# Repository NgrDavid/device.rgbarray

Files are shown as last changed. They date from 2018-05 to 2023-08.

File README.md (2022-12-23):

## Harp RGB Array

Controls 2 arrays of colored LEDs according to RGB scale (Up to 32 LED on each array). Each LED has an associated index.

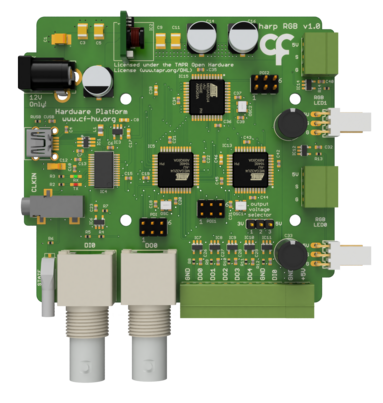
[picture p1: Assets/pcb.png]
harprgbarray


### Key Features ###

* Supports two LED array stripes
* Each stripe can have up to 32 LEDs
* Configurable color and intensity of each LED

### Connectivity ###

* 1x clock sync input (CLKIN) [stereo jack]
* 1x USB (for computer) [USB type C]
* 1x 12V supply [barrel connector jack]
* 1x I/O interface (5x general-purpose digital outputs DO0-DO4, 1x general purpose digital input DI0) [screw terminal]
* 1x digital output (DO0) [BNC]
* 1x digital input (DI0) [BNC]
* 1x Array 0 (G, S, 5V) [flick lock and screw terminal]
* 1x Array 1 (G, S, 5V) [flick lock and screw terminal]

## Interface ##

The interface with the Harp board can be done through [Bonsai](https://bonsai-rx.org/) or a dedicated GUI (Graphical User Interface).

In order to use this GUI, there are some software that needs to be installed:

1 - Install the [drivers](https://bitbucket.org/fchampalimaud/downloads/downloads/UsbDriver-2.12.26.zip).

2 - Install the [runtime](https://bitbucket.org/fchampalimaud/downloads/downloads/Runtime-1.0.zip).

3 - Reboot the computer.

4 - Install the [GUI](https://bitbucket.org/fchampalimaud/downloads/downloads/Harp%20RGB%20Array%20v1.0.0.zip).

## Licensing ##

Each subdirectory will contain a license or, possibly, a set of licenses if it involves both hardware and software.

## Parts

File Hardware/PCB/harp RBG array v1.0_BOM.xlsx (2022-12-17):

Part(s) | Quantity | Description | Distributor | Part. No.
IC1 | 1 | ESD Protection Low Cap | Mouser | 511-USBLC6-2SC6Y
IC2 | 1 | Conversores CC/CC sem isolação 6-A 4.5V-14V Input Non-Iso Adj Pwr Mod | Mouser | 595-PTR08060WVD
IC3 | 1 | LDO 250mA Ultra-Lo Noise LDO Reg | Mouser | 595-LP5907MFX-3.3NPB
IC4 | 1 | IC USB USB to Serial UART Enhanced IC SSOP-28 | Mouser | 895-FT232RL
IC5 | 1 | Microcontroladores de 8 bits - MCU 44TQFP, IND TEMP GREEN, 1.6-3.6V | Mouser | 556-ATXMEGA128A4U-AU
IC13, IC15 | 2 | Microcontroladores de 8 bits - MCU AVR8 32KB FLSH 4KB | Mouser | 556-ATXMEGA32A4U-AU
IC6, IC7, IC8, IC9, IC10, IC11, IC12, IC14 | 8 | Buffers e line drivers 1.65-5.5V Single Non-Inverting TTL | Mouser | 863-M74VHC1GT50DTT1G
C6, C7 | 2 | CAP CER 47pF 50V ±5% C0G 0402 | Mouser | 77-VJ0402A470JXACBC
CUSB | 1 | CAP CER 4.7nF 100V ±10% X7R 0402 | Mouser | 81-GRM155R72A472KA01
C4, C10, C13, C15, C18, C19, C21, C22, C23, C24, C26, C27, C28, C29, C30, C31, C32, C34, C35, C37, C39, C40, C42, C43, C45 | 25 | CAP CER 100nF 10V X5R 0402 | REEL | REEL
C20, C36, C44 | 3 | CAP CER 0.33uF 10V ±10% X5R 0402 | Mouser | GRM155R61A334KE15D
C12 | 1 | CAP TAN 4.7uF 6.3V ±10% 1206 | Mouser | 80-T491A475K006
C8, C17, C25, C38, C46 | 5 | CAP CER 10uF 10V ±10% X5R 0603 | Mouser | 81-GRM188R61A106KE9D
C1 | 1 | CAP TAN 22uF 20V ±10% 1210 | Mouser | 667-20TQC22MYFB
C9 | 1 | CAP CER 22uF 16V ±10% X5R 1210 | Mouser | 81-GRM32ER61C226KE20
C3, C5 | 2 | CAP CER 22uF 25V ±10% X5R 1210 | Mouser | 81-GRM32ER61E226KE15
C2 | 1 | CAP ELE 100uF 25V ±20% | Mouser | 667-25SVF100M
C14, C16 | 2 | CAP ELE 270uF 16V ±20% | Mouser | 667-16SVF270M
C33, C41 | 2 | CAP ELE TH 470uF 16V 20% | Mouser | 667-EEU-FM1C471
R7, R8, R9, R10, R11, R12 | 6 | RES SMD 33Ω 5% 0402 | Mouser | 667-ERJ-2GEJ330X
R6 | 1 | RES SMD 68Ω 5% 0402 | Mouser | 71-CRCW0402-68-E3
R13, R14 | 2 | RES SMD 100Ω 1% 0402 | Mouser | 667-ERJ-2RKF1000X
RTRIM | 1 | RES SMD 267Ω 1% 0402 | Mouser | 667-ERJ-2RKF2670X
R4 | 1 | RES SMD 330Ω 1% 0402 | Mouser | 667-ERJ-PA2F3300X
R5 | 1 | RES SMD 100kΩ 1% 0402 | REEL | REEL
RUSB | 1 | RES SMD 1MΩ 1% 0402 | Mouser | 652-CR0402FX-1004GLF
STATE | 1 | LED, Green, 1.6mm x 0.8mm, 566 nm, 2.1 V, 20 mA, 15 mcd | Mouser | 78-TLMP1100-GS08
OSC, OSC1, OSC2 | 3 | 32MHz 10ppm | Mouser | 998-1001CI5032.0000T
CLKIN | 1 | SMT 3.5 STEREO REEL | Mouser | 502-35RASMT2BHNTRX
L1 | 1 | 40ohms 100MHz 1.5A Monolithic 0805 SMD | Mouser | 875-MI0805K400R-10
L2 | 1 | FERRITE BEAD 600Ω 500mA 300mΩ 0805 | Mouser | 875-HZ0805E601R-10
PDI, PDI1, PDI2 | 3 | 6P DR UNSHRD HRD | Mouser | 649-67996-206HLF
USB | 1 | UX60-MB-5S8 | Mouser | 798-UX60-MB-5S8
USB Cable | 1 | USB A - MINI-B 1M BLACK | Mouser | 538-88732-8602
 | 1 | Tubos de Luz LED CML LIGHTPIPE | Mouser | 606-7513D2-L
JACK | 1 | CC PCB 2.1MM | Mouser | 163-179PH-EX
IN1, OUT1 | 2 | Connectores RF / Connectores Coaxiais R.A. JACK 50 OHM | Mouser | 571-5227161-1
JP1 | 1 | 3POS Gold Male | Mouser | 649-68001-203HLF
 | 1 | SHUNT JUMPER, 2POS | Farnell | 2396301
WALL ADAPTER | 1 | AC/DC Power Supply, Level VI, Wall Mount, 1 Output, 24 W, 12 V, 2 A | Farnell | 2643258
J1, J2 | 2 | Right Angle, 2.54 mm, 3 Contacts, Header, KK 7395 Series, Through Hole | Farnell | 1360143
X2 | 1 | 20.1550M/2-E - Pluggable Terminal Block, 3.5 mm, 2 Ways, 28 AWG, 16 AWG, 1.5 mm², Screw | Farnell | 2575215
X3, X4 | 2 | 20.1550M/3-E - Pluggable Terminal Block, 3.5 mm, 3 Ways, 28 AWG, 16 AWG, 1.5 mm², Screw | Farnell | 2575216
X1 | 1 | 20.1550M/8-E - Pluggable Terminal Block, 3.5 mm, 8 Ways, 28 AWG, 16 AWG, 1.5 mm², Screw | Farnell | 2575220
 | 1 | 20.155MH/3-E - Terminal Block, Horizontal, Header, 3.5 mm, 3 Ways, 10 A | Farnell | 2517859
 | 2 | 20.155MH/2-E - Terminal Block, Horizontal, Header, 3.5 mm, 2 Ways, 10 A | Farnell | 2517858
 | 1 | 20.155MH/8-E - Terminal Block, Horizontal, Header, 3.5 mm, 8 Ways, 10 A | Farnell | 2517863
 | 8 | 1110030 - Nut, Hex, M3, Nylon 6.6, Pack of 50 | Farnell | 1110030
 | 4 | Machine Screw, M3, 10 mm, Nylon (Polyamide), Pan Head Slotted, PK25 | Farnell | 1514410
Components | 115
Licensed under the TAPR Open Hardware License (www.tapr.org/OHL)
Copyright 2017 Artur Silva and Filipe Carvalho

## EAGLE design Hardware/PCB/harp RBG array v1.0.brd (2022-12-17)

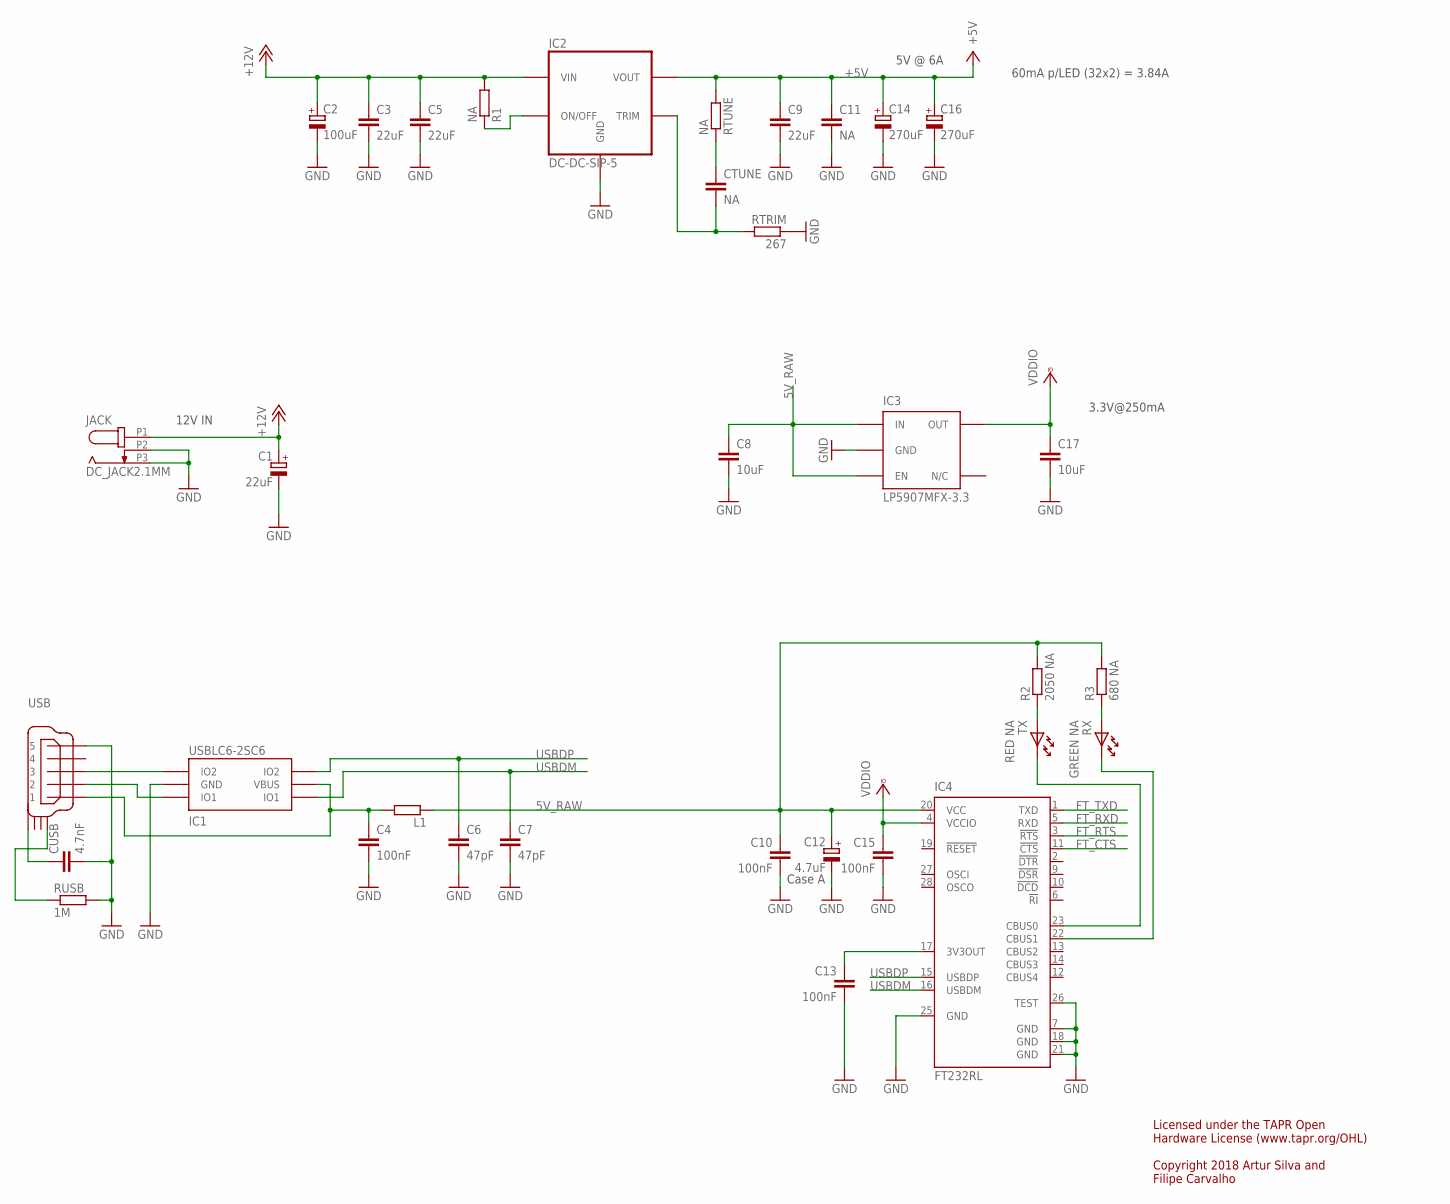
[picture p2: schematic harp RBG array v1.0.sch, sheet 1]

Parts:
C1: 22uF; CAP_100UF_HAND
C2: 100uF; PANASONIC_E
C3, C5, C9: 22uF; C1210
C4, C10, C13, C15: 100nF; C0402
C6, C7: 47pF; C0402
C8, C17: 10uF; C0603
C11: NA; C1210
C12: 4.7uF; A/3216-18W
C14, C16: 270uF; PANASONIC_E
CTUNE: NA; C0402
CUSB: 4.7nF; C0402
IC1: USBLC6-2SC6; SOT23-6L
IC2: DC-DC-SIP-5; SIP-5
IC3: LP5907MFX-3.3; TSOT23-5
IC4: FT232RL; SSOP28
JACK: DC_JACK2.1MM; DC_POWER_INPUT_2.1MM
L1: ???; R0805
R1: NA; R0402
R2: 2050 NA; R0402
R3: 680 NA; R0402
RTRIM: 267; R0402
RTUNE: NA; R0402
RUSB: 1M; R0402
RX: GREEN NA; LED_HAND
TX: RED NA; LED_HAND
USB: USB_MINI_B; 240-0002-1

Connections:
5V_RAW: C8.1, C10.1, C12.+, IC3.1 (IN), IC3.3 (EN), IC4.20 (VCC), L1.1, R2.2, R3.2
+5V: C9.1, C11.1, C14.+, C16.+, IC2.P4 (VOUT), RTUNE.2; also elsewhere on the board
+12V: C1.+, C2.+, C3.1, C5.1, IC2.P2 (VIN), JACK.P1 (1), R1.2
FT_CTS: IC4.11 (!CTS); also elsewhere on the board
FT_RTS: IC4.3 (!RTS); also elsewhere on the board
FT_RXD: IC4.5 (RXD); also elsewhere on the board
FT_TXD: IC4.1 (TXD); also elsewhere on the board
GND: C1.-, C2.-, C3.2, C4.2, C5.2, C6.2, C7.2, C8.2, C9.2, C10.2, C11.2, C12.-, C13.2, C14.-, C15.2, C16.-, C17.2, CUSB.2, IC1.P$2 (GND), IC2.P3 (GND), IC3.2 (GND), IC4.7 (GND), IC4.18 (GND), IC4.21 (GND), IC4.25 (GND), IC4.26 (TEST), JACK.P2 (2), JACK.P3 (3), RTRIM.1, RUSB.2, USB.P$5 (5); also elsewhere on the board
unnamed: CTUNE.2, IC2.P5 (TRIM), RTRIM.2
unnamed: CTUNE.1, RTUNE.1
unnamed: IC2.P1 (ON/OFF), R1.1
unnamed: C13.1, IC4.17 (3V3OUT)
unnamed: C4.1, IC1.P$5 (VBUS), L1.2, USB.P$1 (1)
unnamed: IC1.P$1 (IO1), USB.P$2 (2)
unnamed: R3.1, RX.A
unnamed: IC4.23 (CBUS0), TX.K
unnamed: IC4.22 (CBUS1), RX.K
unnamed: IC1.P$3 (IO2), USB.P$3 (3)
unnamed: CUSB.1, USB.SHIELD_4
unnamed: RUSB.1, USB.SHIELD_1
unnamed: R2.1, TX.A
USBDM: C7.1, IC1.P$6 (IO1), IC4.16 (USBDM)
USBDP: C6.1, IC1.P$4 (IO2), IC4.15 (USBDP)
VCCIO: C15.1, C17.1, IC3.5 (OUT), IC4.4 (VCCIO); also elsewhere on the board

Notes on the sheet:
Case A
3.3V@250mA
Licensed under the TAPR Open Hardware License (www.tapr.org/OHL) Copyright 2018 Artur Silva and Filipe Carvalho
12V IN
5V @ 6A
60mA p/LED (32x2) = 3.84A

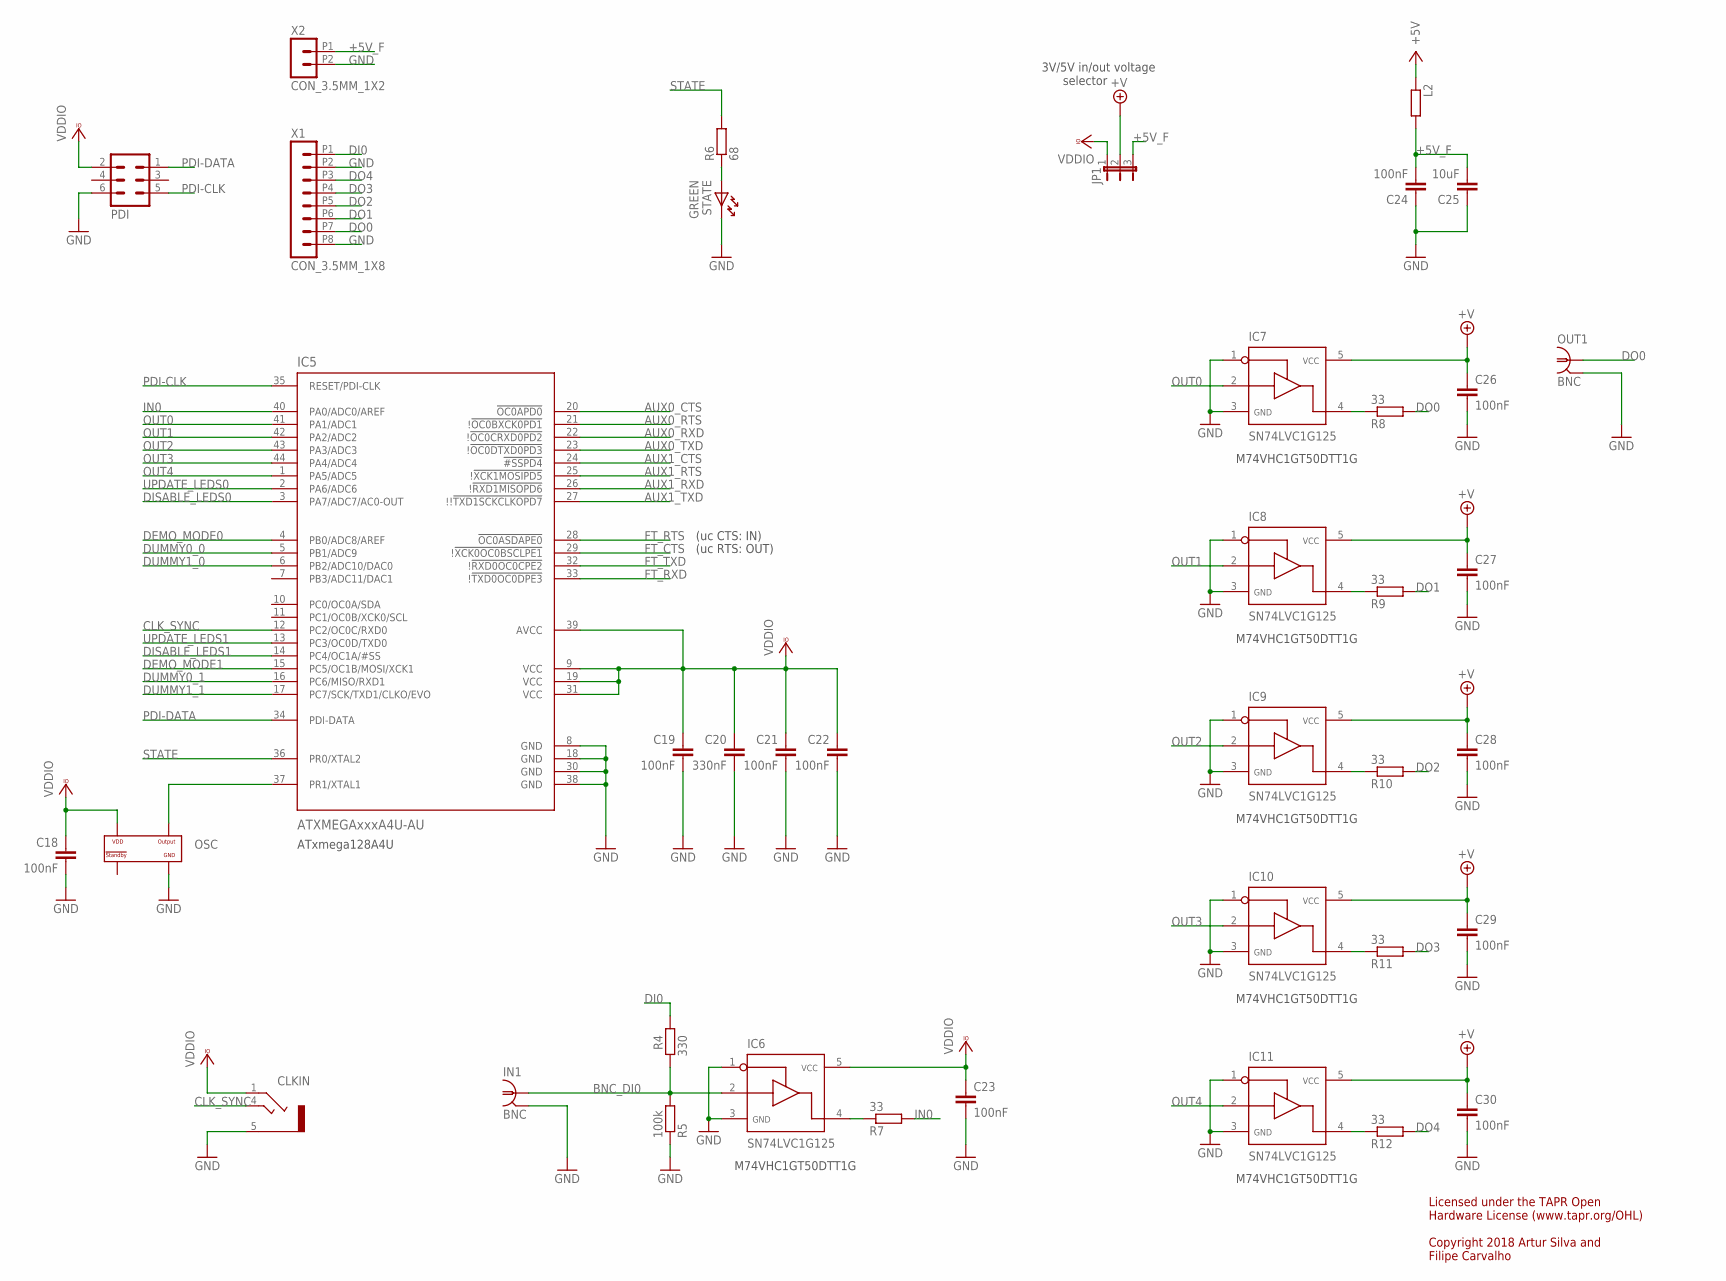
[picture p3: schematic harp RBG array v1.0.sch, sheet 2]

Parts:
C18, C19, C21, C22, C23, C24, C26, C27, C28, C29, C30: 100nF; C0402
C20: 330nF; C0402
C25: 10uF; C0603
CLKIN: STEREO_JACK; 35RASMT2BHNTRX
IC5: ATXMEGAxxxA4U-AU; QFP80P1200X1200X120-44N
IC6, IC7, IC8, IC9, IC10, IC11: SN74LVC1G125; SOT23-5
IN1: BNC; BNC_RA
JP1: JP2E; JP2
L2: 600@100M; R0805
OSC: OSCILLATOR; OSCILLATOR_3.2X2.5
OUT1: BNC; BNC_RA
PDI: MA03-2
R4: 330; R0402
R5: 100k; R0402
R6: 68; R0402
R7, R8, R9, R10, R11, R12: 33; R0402
STATE: GREEN; LED_HAND
X1: CON_3.5MM_1X8
X2: CON_3.5MM_1X2

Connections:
+5V: L2.1; also elsewhere on the board
+5V_F: C24.2, C25.2, JP1.3, L2.2, X2.P1 (1)
+V: C26.1, C27.1, C28.1, C29.1, C30.1, IC7.5, IC8.5, IC9.5, IC10.5, IC11.5, JP1.2
AUX0_CTS: IC5.20 (!OC0APD0); also elsewhere on the board
AUX0_RTS: IC5.21 (!!OC0BXCK0PD1); also elsewhere on the board
AUX0_RXD: IC5.22 (!!OC0CRXD0PD2); also elsewhere on the board
AUX0_TXD: IC5.23 (!!OC0DTXD0PD3); also elsewhere on the board
AUX1_CTS: IC5.24 (!#SSPD4); also elsewhere on the board
AUX1_RTS: IC5.25 (!!XCK1MOSIPD5); also elsewhere on the board
AUX1_RXD: IC5.26 (!!RXD1MISOPD6); also elsewhere on the board
AUX1_TXD: IC5.27 (!!!TXD1SCKCLKOPD7); also elsewhere on the board
BNC_DI0: IC6.2, IN1.1, R4.2, R5.2
CLK_SYNC: CLKIN.4, IC5.12 (PC2/OC0C/RXD0)
DEMO_MODE0: IC5.4 (PB0/ADC8/AREF); also elsewhere on the board
DEMO_MODE1: IC5.15 (PC5/OC1B/MOSI/XCK1); also elsewhere on the board
DI0: R4.1, X1.P1 (1)
DISABLE_LEDS0: IC5.3 (PA7/ADC7/AC0-OUT); also elsewhere on the board
DISABLE_LEDS1: IC5.14 (PC4/OC1A/#SS); also elsewhere on the board
DO0: OUT1.1, R8.2, X1.P7 (7)
DO1: R9.2, X1.P6 (6)
DO2: R10.2, X1.P5 (5)
DO3: R11.2, X1.P4 (4)
DO4: R12.2, X1.P3 (3)
DUMMY0_0: IC5.5 (PB1/ADC9); also elsewhere on the board
DUMMY0_1: IC5.16 (PC6/MISO/RXD1); also elsewhere on the board
DUMMY1_0: IC5.6 (PB2/ADC10/DAC0); also elsewhere on the board
DUMMY1_1: IC5.17 (PC7/SCK/TXD1/CLKO/EVO); also elsewhere on the board
FT_CTS: IC5.29 (!!XCK0OC0BSCLPE1); also elsewhere on the board
FT_RTS: IC5.28 (!OC0ASDAPE0); also elsewhere on the board
FT_RXD: IC5.33 (!!TXD0OC0DPE3); also elsewhere on the board
FT_TXD: IC5.32 (!!RXD0OC0CPE2); also elsewhere on the board
GND: C18.2, C19.2, C20.2, C21.2, C22.2, C23.2, C24.1, C25.1, C26.2, C27.2, C28.2, C29.2, C30.2, CLKIN.5, IC5.8 (GND), IC5.18 (GND), IC5.30 (GND), IC5.38 (GND), IC6.1, IC6.3, IC7.1, IC7.3, IC8.1, IC8.3, IC9.1, IC9.3, IC10.1, IC10.3, IC11.1, IC11.3, IN1.2, OSC.P$2 (GND), OUT1.2, PDI.6, R5.1, STATE.K, X1.P2 (2), X1.P8 (8), X2.P2 (2); also elsewhere on the board
IN0: IC5.40 (PA0/ADC0/AREF), R7.2
unnamed: IC6.4, R7.1
unnamed: IC8.4, R9.1
unnamed: IC7.4, R8.1
unnamed: IC9.4, R10.1
unnamed: IC10.4, R11.1
unnamed: IC11.4, R12.1
unnamed: R6.1, STATE.A
OSC2: IC5.37 (PR1/XTAL1), OSC.P$3 (OUTPUT)
OUT0: IC5.41 (PA1/ADC1), IC7.2
OUT1: IC5.42 (PA2/ADC2), IC8.2
OUT2: IC5.43 (PA3/ADC3), IC9.2
OUT3: IC5.44 (PA4/ADC4), IC10.2
OUT4: IC5.1 (PA5/ADC5), IC11.2
PDI-CLK: IC5.35 (RESET/PDI-CLK), PDI.5
PDI-DATA: IC5.34 (PDI-DATA), PDI.1
STATE: IC5.36 (PR0/XTAL2), R6.2
UPDATE_LEDS0: IC5.2 (PA6/ADC6); also elsewhere on the board
UPDATE_LEDS1: IC5.13 (PC3/OC0D/TXD0); also elsewhere on the board
VCCIO: C18.1, C19.1, C20.1, C21.1, C22.1, C23.1, CLKIN.1, IC5.9 (VCC), IC5.19 (VCC), IC5.31 (VCC), IC5.39 (AVCC), IC6.5, JP1.1, OSC.P$4 (VDD), PDI.2; also elsewhere on the board

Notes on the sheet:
Licensed under the TAPR Open Hardware License (www.tapr.org/OHL) Copyright 2018 Artur Silva and Filipe Carvalho
(uc CTS: IN)
(uc RTS: OUT)
M74VHC1GT50DTT1G
3V/5V in/out voltage selector
ATxmega128A4U

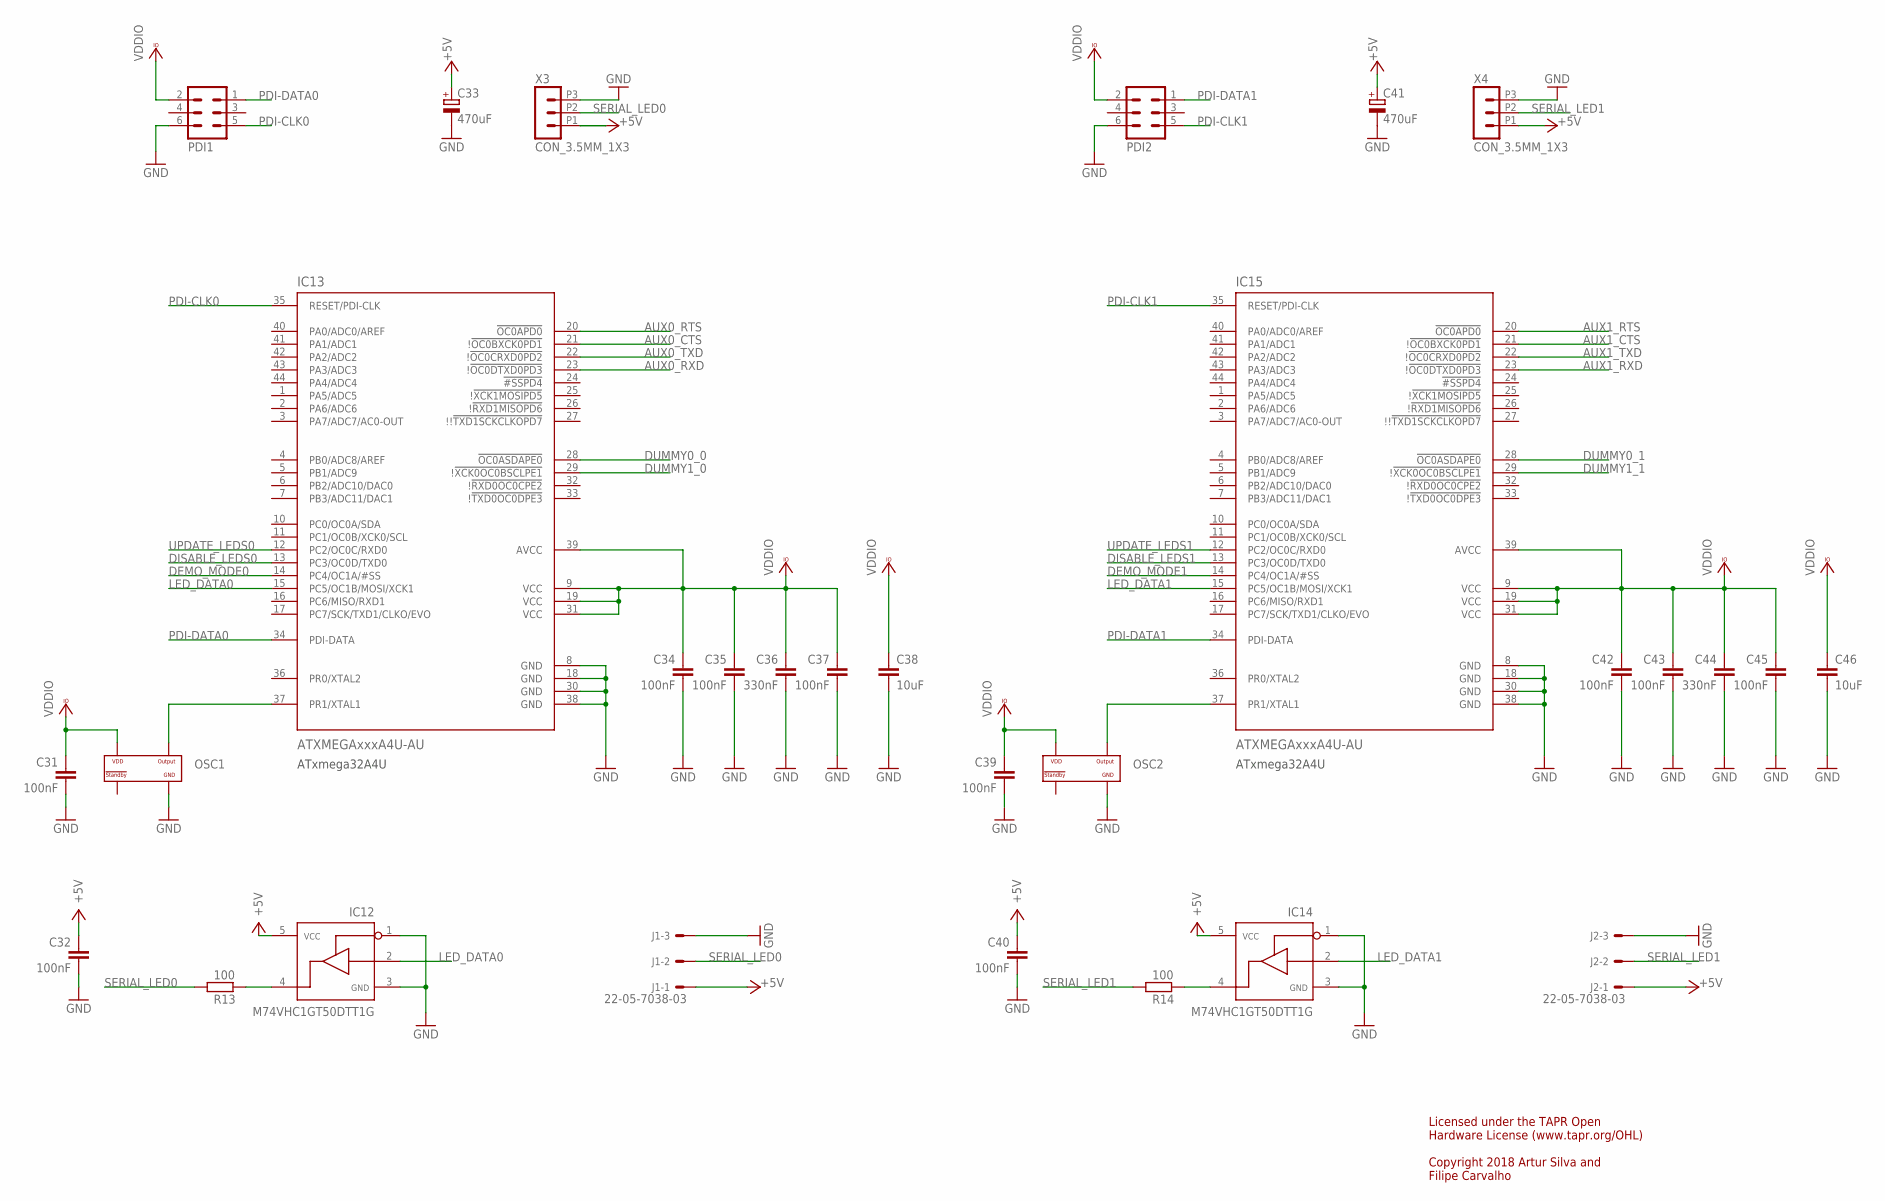
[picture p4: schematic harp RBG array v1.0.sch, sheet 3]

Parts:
C31, C32, C34, C35, C37, C39, C40, C42, C43, C45: 100nF; C0402
C33, C41: 470uF; E3,5-8
C36, C44: 330nF; C0402
C38, C46: 10uF; C0603
IC12, IC14: M74VHC1GT50DTT1G; SOT23-5
IC13, IC15: ATXMEGAxxxA4U-AU; QFP80P1200X1200X120-44N
J1, J2: 22-05-7038-03; 7395-03
OSC1, OSC2: OSCILLATOR; OSCILLATOR_3.2X2.5
PDI1, PDI2: MA03-2
R13, R14: 100; R0402
X3, X4: CON_3.5MM_1X3

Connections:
+5V: C32.1, C33.+, C40.1, C41.+, IC12.5, IC14.5, J1.1, J2.1, X3.P1 (1), X4.P1 (1); also elsewhere on the board
AUX0_CTS: IC13.21 (!!OC0BXCK0PD1); also elsewhere on the board
AUX0_RTS: IC13.20 (!OC0APD0); also elsewhere on the board
AUX0_RXD: IC13.23 (!!OC0DTXD0PD3); also elsewhere on the board
AUX0_TXD: IC13.22 (!!OC0CRXD0PD2); also elsewhere on the board
AUX1_CTS: IC15.21 (!!OC0BXCK0PD1); also elsewhere on the board
AUX1_RTS: IC15.20 (!OC0APD0); also elsewhere on the board
AUX1_RXD: IC15.23 (!!OC0DTXD0PD3); also elsewhere on the board
AUX1_TXD: IC15.22 (!!OC0CRXD0PD2); also elsewhere on the board
DEMO_MODE0: IC13.14 (PC4/OC1A/#SS); also elsewhere on the board
DEMO_MODE1: IC15.14 (PC4/OC1A/#SS); also elsewhere on the board
DISABLE_LEDS0: IC13.13 (PC3/OC0D/TXD0); also elsewhere on the board
DISABLE_LEDS1: IC15.13 (PC3/OC0D/TXD0); also elsewhere on the board
DUMMY0_0: IC13.28 (!OC0ASDAPE0); also elsewhere on the board
DUMMY0_1: IC15.28 (!OC0ASDAPE0); also elsewhere on the board
DUMMY1_0: IC13.29 (!!XCK0OC0BSCLPE1); also elsewhere on the board
DUMMY1_1: IC15.29 (!!XCK0OC0BSCLPE1); also elsewhere on the board
GND: C31.2, C32.2, C33.-, C34.2, C35.2, C36.2, C37.2, C38.2, C39.2, C40.2, C41.-, C42.2, C43.2, C44.2, C45.2, C46.2, IC12.1, IC12.3, IC13.8 (GND), IC13.18 (GND), IC13.30 (GND), IC13.38 (GND), IC14.1, IC14.3, IC15.8 (GND), IC15.18 (GND), IC15.30 (GND), IC15.38 (GND), J1.3, J2.3, OSC1.P$2 (GND), OSC2.P$2 (GND), PDI1.6, PDI2.6, X3.P3 (3), X4.P3 (3); also elsewhere on the board
LED_DATA0: IC12.2, IC13.15 (PC5/OC1B/MOSI/XCK1)
LED_DATA1: IC14.2, IC15.15 (PC5/OC1B/MOSI/XCK1)
unnamed: IC14.4, R14.2
unnamed: IC12.4, R13.2
OSC1: IC13.37 (PR1/XTAL1), OSC1.P$3 (OUTPUT)
OSC3: IC15.37 (PR1/XTAL1), OSC2.P$3 (OUTPUT)
PDI-CLK0: IC13.35 (RESET/PDI-CLK), PDI1.5
PDI-CLK1: IC15.35 (RESET/PDI-CLK), PDI2.5
PDI-DATA0: IC13.34 (PDI-DATA), PDI1.1
PDI-DATA1: IC15.34 (PDI-DATA), PDI2.1
SERIAL_LED0: J1.2, R13.1, X3.P2 (2)
SERIAL_LED1: J2.2, R14.1, X4.P2 (2)
UPDATE_LEDS0: IC13.12 (PC2/OC0C/RXD0); also elsewhere on the board
UPDATE_LEDS1: IC15.12 (PC2/OC0C/RXD0); also elsewhere on the board
VCCIO: C31.1, C34.1, C35.1, C36.1, C37.1, C38.1, C39.1, C42.1, C43.1, C44.1, C45.1, C46.1, IC13.9 (VCC), IC13.19 (VCC), IC13.31 (VCC), IC13.39 (AVCC), IC15.9 (VCC), IC15.19 (VCC), IC15.31 (VCC), IC15.39 (AVCC), OSC1.P$4 (VDD), OSC2.P$4 (VDD), PDI1.2, PDI2.2; also elsewhere on the board

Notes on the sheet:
ATxmega32A4U
Licensed under the TAPR Open Hardware License (www.tapr.org/OHL) Copyright 2018 Artur Silva and Filipe Carvalho

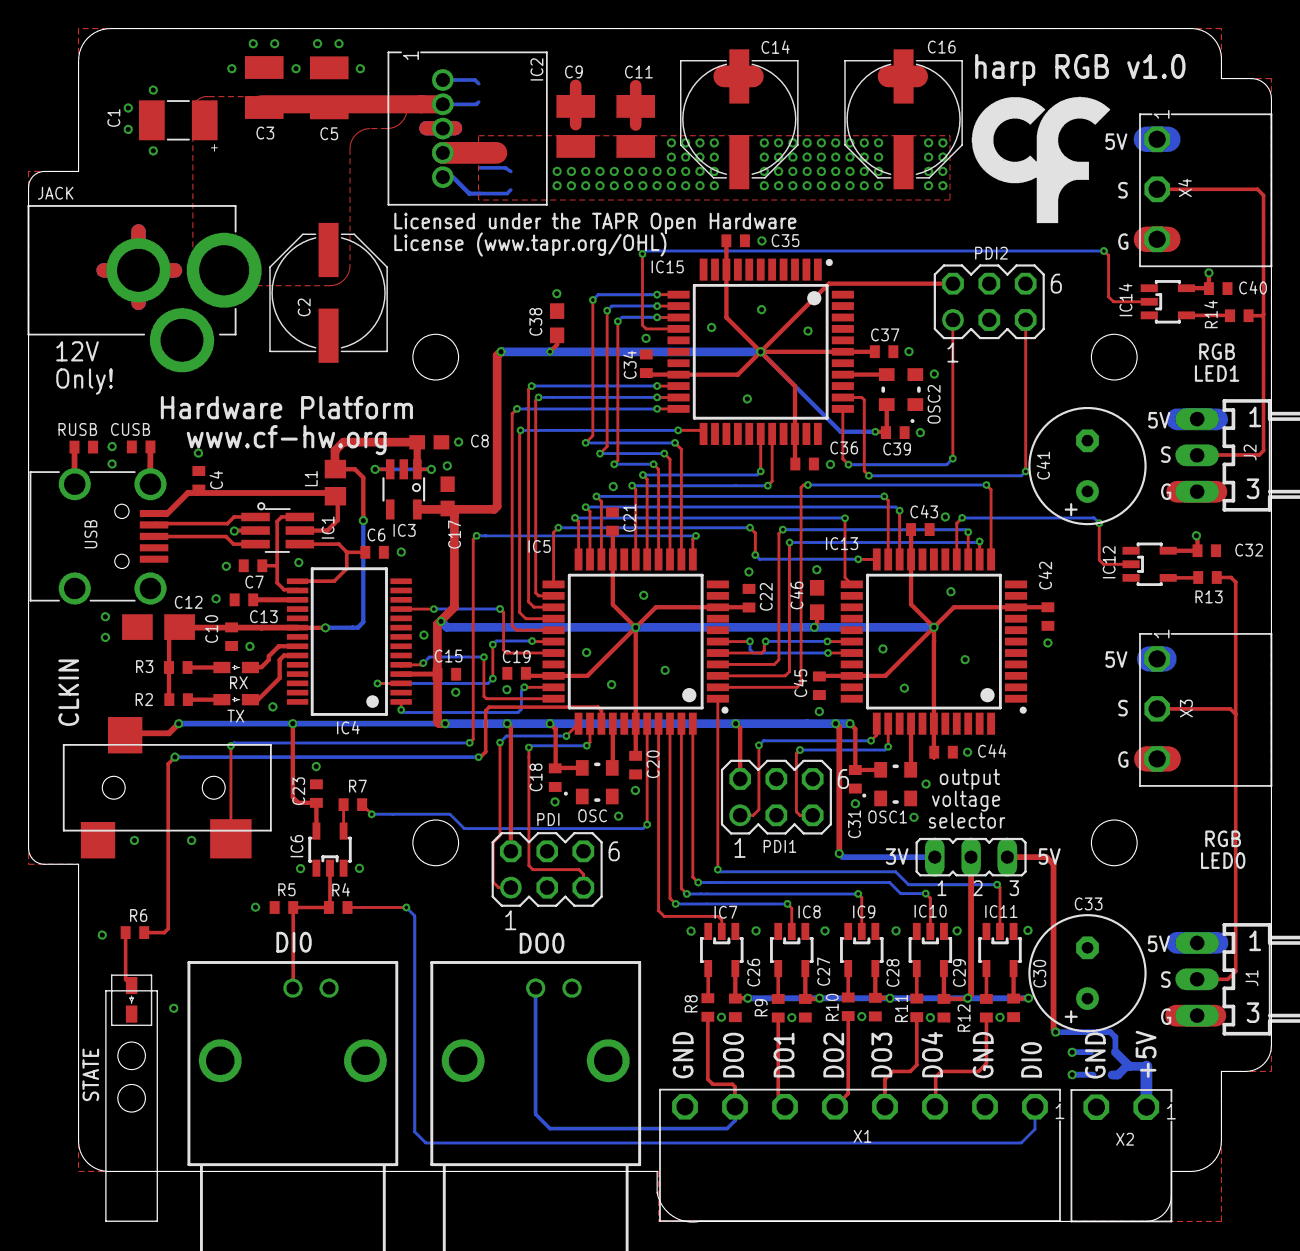
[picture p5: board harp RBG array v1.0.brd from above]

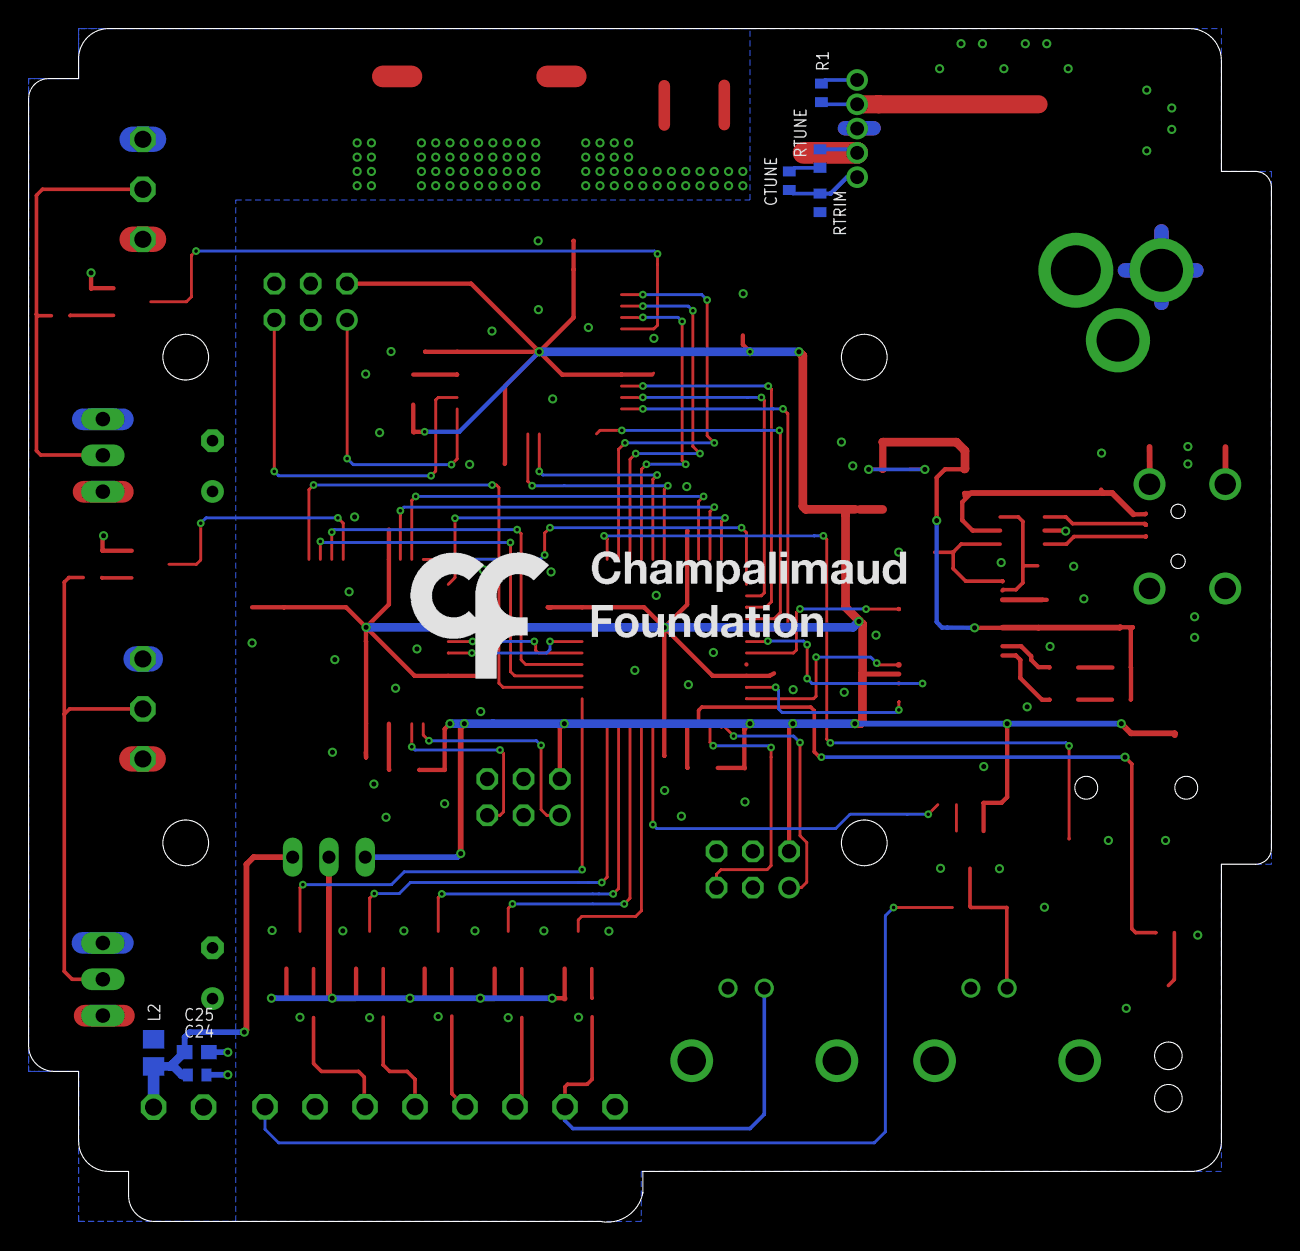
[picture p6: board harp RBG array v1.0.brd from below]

Board: 2 copper layers, 87.0 x 83.5 mm, 106 parts (8 on the bottom side), 81 nets.

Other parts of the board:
U$1: LED_PIPE_7513D2-L
U$3: LOGO_5
U$9: LOGO_6

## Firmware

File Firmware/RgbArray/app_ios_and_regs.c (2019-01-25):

#include <avr/io.h>
#include "hwbp_core_types.h"
#include "app_ios_and_regs.h"

/************************************************************************/
/* Configure and initialize IOs                                         */
/************************************************************************/
void init_ios(void)
{	/* Configure input pins */
	io_pin2in(&PORTA, 0, PULL_IO_UP, SENSE_IO_EDGES_BOTH);               // DI0
	io_pin2in(&PORTB, 1, PULL_IO_DOWN, SENSE_IO_EDGES_BOTH);             // DUMMY0_0
	io_pin2in(&PORTB, 2, PULL_IO_DOWN, SENSE_IO_EDGES_BOTH);             // DUMMY1_0
	io_pin2in(&PORTC, 6, PULL_IO_DOWN, SENSE_IO_EDGES_BOTH);             // DUMMY0_1
	io_pin2in(&PORTC, 7, PULL_IO_DOWN, SENSE_IO_EDGES_BOTH);             // DUMMY1_1

	/* Configure input interrupts */
	io_set_int(&PORTA, INT_LEVEL_LOW, 0, (1<<0), false);                 // DI0

	/* Configure output pins */
	io_pin2out(&PORTA, 1, OUT_IO_DIGITAL, IN_EN_IO_EN);                  // DO0
	io_pin2out(&PORTA, 2, OUT_IO_DIGITAL, IN_EN_IO_EN);                  // DO1
	io_pin2out(&PORTA, 3, OUT_IO_DIGITAL, IN_EN_IO_EN);                  // DO2
	io_pin2out(&PORTA, 4, OUT_IO_DIGITAL, IN_EN_IO_EN);                  // DO3
	io_pin2out(&PORTA, 5, OUT_IO_DIGITAL, IN_EN_IO_EN);                  // DO4
	io_pin2out(&PORTA, 6, OUT_IO_DIGITAL, IN_EN_IO_EN);                  // UPDATE_LEDS0
	io_pin2out(&PORTA, 7, OUT_IO_DIGITAL, IN_EN_IO_EN);                  // DISABLE_LEDS0
	io_pin2out(&PORTC, 3, OUT_IO_DIGITAL, IN_EN_IO_EN);                  // UPDATE_LEDS1
	io_pin2out(&PORTC, 4, OUT_IO_DIGITAL, IN_EN_IO_EN);                  // DISABLE_LEDS1
	io_pin2out(&PORTB, 0, OUT_IO_DIGITAL, IN_EN_IO_EN);                  // DEMO_MODE0
	io_pin2out(&PORTC, 5, OUT_IO_DIGITAL, IN_EN_IO_EN);                  // DEMO_MODE1
	io_pin2out(&PORTB, 0, OUT_IO_DIGITAL, IN_EN_IO_EN);                  // DEMO_MODE0
	io_pin2out(&PORTC, 5, OUT_IO_DIGITAL, IN_EN_IO_EN);                  // DEMO_MODE1

	/* Initialize output pins */
	clr_DO0;
	clr_DO1;
	clr_DO2;
	clr_DO3;
	clr_DO4;
	clr_UPDATE_LEDS0;
	clr_DISABLE_LEDS0;
	clr_UPDATE_LEDS1;
	clr_DISABLE_LEDS1;
	clr_DEMO_MODE0;
	clr_DEMO_MODE1;
	clr_DEMO_MODE0;
	clr_DEMO_MODE1;
}

/************************************************************************/
/* Registers' stuff                                                     */
/************************************************************************/
AppRegs app_regs;

uint8_t app_regs_type[] = {
	TYPE_U8,
	TYPE_U8,
	TYPE_U8,
	TYPE_U8,
	TYPE_U8,
	TYPE_U8,
	TYPE_U8,
	TYPE_U8,
	TYPE_U8,
	TYPE_U8,
	TYPE_U8,
	TYPE_U8,
	TYPE_U8,
	TYPE_U8,
	TYPE_U8,
	TYPE_U8,
	TYPE_U8,
	TYPE_U16,
	TYPE_U8,
	TYPE_U8
};

uint16_t app_regs_n_elements[] = {
	1,
	1,
	192,
	96,
	96,
	3,
	1,
	1,
	1,
	1,
	1,
	1,
	1,
	1,
	1,
	1,
	1,
	1,
	1,
	1
};

uint8_t *app_regs_pointer[] = {
	(uint8_t*)(&app_regs.REG_LEDS_STATUS),
	(uint8_t*)(&app_regs.REG_LEDS_ON_BUS),
	(uint8_t*)(app_regs.REG_COLOR_ARRAY),
	(uint8_t*)(app_regs.REG_COLOR_ARRAY_BUS0),
	(uint8_t*)(app_regs.REG_COLOR_ARRAY_BUS1),
	(uint8_t*)(app_regs.REG_COLOR_OFF),
	(uint8_t*)(&app_regs.REG_RESERVED1),
	(uint8_t*)(&app_regs.REG_DI0_CONF),
	(uint8_t*)(&app_regs.REG_DO0_CONF),
	(uint8_t*)(&app_regs.REG_DO1_CONF),
	(uint8_t*)(&app_regs.REG_RESERVED2),
	(uint8_t*)(&app_regs.REG_LATCH_NEXT_UPDATE),
	(uint8_t*)(&app_regs.REG_INPUTS_STATE),
	(uint8_t*)(&app_regs.REG_OUTPUTS_SET),
	(uint8_t*)(&app_regs.REG_OUTPUTS_CLEAR),
	(uint8_t*)(&app_regs.REG_OUTPUTS_TOGGLE),
	(uint8_t*)(&app_regs.REG_OUTPUTS_OUT),
	(uint8_t*)(&app_regs.REG_PULSE_PERIOD),
	(uint8_t*)(&app_regs.REG_PULSE_COUNT),
	(uint8_t*)(&app_regs.REG_EVNT_ENABLE)
};

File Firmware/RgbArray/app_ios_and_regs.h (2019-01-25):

#ifndef _APP_IOS_AND_REGS_H_
#define _APP_IOS_AND_REGS_H_
#include "cpu.h"

void init_ios(void);
/************************************************************************/
/* Definition of input pins                                             */
/************************************************************************/
// DI0                    Description: Input DIO
// DUMMY0_0               Description: Not used
// DUMMY1_0               Description: Not used
// DUMMY0_1               Description: Not used
// DUMMY1_1               Description: Not used

#define read_DI0 read_io(PORTA, 0)              // DI0
#define read_DUMMY0_0 read_io(PORTB, 1)         // DUMMY0_0
#define read_DUMMY1_0 read_io(PORTB, 2)         // DUMMY1_0
#define read_DUMMY0_1 read_io(PORTC, 6)         // DUMMY0_1
#define read_DUMMY1_1 read_io(PORTC, 7)         // DUMMY1_1

/************************************************************************/
/* Definition of output pins                                            */
/************************************************************************/
// DO0                    Description: Output DO0
// DO1                    Description: Output DO1
// DO2                    Description: Output DO2
// DO3                    Description: Output DO3
// DO4                    Description: Output DO4
// UPDATE_LEDS0           Description: Update the RGBs on Bus 0
// DISABLE_LEDS0          Description: Turn OFF the RGBs on Bus 0
// UPDATE_LEDS1           Description: Update the RGBs on Bus 1
// DISABLE_LEDS1          Description: Turn OFF the RGBs on Bus 1
// DEMO_MODE0             Description: Enable demonstration mode on Bus 0
// DEMO_MODE1             Description: Enable demonstration mode on Bus 1
// DEMO_MODE0             Description: Enable demonstration mode on Bus 0
// DEMO_MODE1             Description: Enable demonstration mode on Bus 1

/* DO0 */
#define set_DO0 set_io(PORTA, 1)
#define clr_DO0 clear_io(PORTA, 1)
#define tgl_DO0 toggle_io(PORTA, 1)
#define read_DO0 read_io(PORTA, 1)

/* DO1 */
#define set_DO1 set_io(PORTA, 2)
#define clr_DO1 clear_io(PORTA, 2)
#define tgl_DO1 toggle_io(PORTA, 2)
#define read_DO1 read_io(PORTA, 2)

/* DO2 */
#define set_DO2 set_io(PORTA, 3)
#define clr_DO2 clear_io(PORTA, 3)
#define tgl_DO2 toggle_io(PORTA, 3)
#define read_DO2 read_io(PORTA, 3)

/* DO3 */
#define set_DO3 set_io(PORTA, 4)
#define clr_DO3 clear_io(PORTA, 4)
#define tgl_DO3 toggle_io(PORTA, 4)
#define read_DO3 read_io(PORTA, 4)

/* DO4 */
#define set_DO4 set_io(PORTA, 5)
#define clr_DO4 clear_io(PORTA, 5)
#define tgl_DO4 toggle_io(PORTA, 5)
#define read_DO4 read_io(PORTA, 5)

/* UPDATE_LEDS0 */
#define set_UPDATE_LEDS0 set_io(PORTA, 6)
#define clr_UPDATE_LEDS0 clear_io(PORTA, 6)
#define tgl_UPDATE_LEDS0 toggle_io(PORTA, 6)
#define read_UPDATE_LEDS0 read_io(PORTA, 6)

/* DISABLE_LEDS0 */
#define set_DISABLE_LEDS0 set_io(PORTA, 7)
#define clr_DISABLE_LEDS0 clear_io(PORTA, 7)
#define tgl_DISABLE_LEDS0 toggle_io(PORTA, 7)
#define read_DISABLE_LEDS0 read_io(PORTA, 7)

/* UPDATE_LEDS1 */
#define set_UPDATE_LEDS1 set_io(PORTC, 3)
#define clr_UPDATE_LEDS1 clear_io(PORTC, 3)
#define tgl_UPDATE_LEDS1 toggle_io(PORTC, 3)
#define read_UPDATE_LEDS1 read_io(PORTC, 3)

/* DISABLE_LEDS1 */
#define set_DISABLE_LEDS1 set_io(PORTC, 4)
#define clr_DISABLE_LEDS1 clear_io(PORTC, 4)
#define tgl_DISABLE_LEDS1 toggle_io(PORTC, 4)
#define read_DISABLE_LEDS1 read_io(PORTC, 4)

/* DEMO_MODE0 */
#define set_DEMO_MODE0 set_io(PORTB, 0)
#define clr_DEMO_MODE0 clear_io(PORTB, 0)
#define tgl_DEMO_MODE0 toggle_io(PORTB, 0)
#define read_DEMO_MODE0 read_io(PORTB, 0)

/* DEMO_MODE1 */
#define set_DEMO_MODE1 set_io(PORTC, 5)
#define clr_DEMO_MODE1 clear_io(PORTC, 5)
#define tgl_DEMO_MODE1 toggle_io(PORTC, 5)
#define read_DEMO_MODE1 read_io(PORTC, 5)

/* DEMO_MODE0 */
#define set_DEMO_MODE0 set_io(PORTB, 0)
#define clr_DEMO_MODE0 clear_io(PORTB, 0)
#define tgl_DEMO_MODE0 toggle_io(PORTB, 0)
#define read_DEMO_MODE0 read_io(PORTB, 0)

/* DEMO_MODE1 */
#define set_DEMO_MODE1 set_io(PORTC, 5)
#define clr_DEMO_MODE1 clear_io(PORTC, 5)
#define tgl_DEMO_MODE1 toggle_io(PORTC, 5)
#define read_DEMO_MODE1 read_io(PORTC, 5)


/************************************************************************/
/* Registers' structure                                                 */
/************************************************************************/
typedef struct
{
	uint8_t REG_LEDS_STATUS;
	uint8_t REG_LEDS_ON_BUS;
	uint8_t REG_COLOR_ARRAY[192];
	uint8_t REG_COLOR_ARRAY_BUS0[96];
	uint8_t REG_COLOR_ARRAY_BUS1[96];
	uint8_t REG_COLOR_OFF[3];
	uint8_t REG_RESERVED1;
	uint8_t REG_DI0_CONF;
	uint8_t REG_DO0_CONF;
	uint8_t REG_DO1_CONF;
	uint8_t REG_RESERVED2;
	uint8_t REG_LATCH_NEXT_UPDATE;
	uint8_t REG_INPUTS_STATE;
	uint8_t REG_OUTPUTS_SET;
	uint8_t REG_OUTPUTS_CLEAR;
	uint8_t REG_OUTPUTS_TOGGLE;
	uint8_t REG_OUTPUTS_OUT;
	uint16_t REG_PULSE_PERIOD;
	uint8_t REG_PULSE_COUNT;
	uint8_t REG_EVNT_ENABLE;
} AppRegs;

/************************************************************************/
/* Registers' address                                                   */
/************************************************************************/
/* Registers */
#define ADD_REG_LEDS_STATUS                 32 // U8     Status of the LEDs and control.
#define ADD_REG_LEDS_ON_BUS                 33 // U8     Number of RGB LEDs used on each bus (Max. is 32)
#define ADD_REG_COLOR_ARRAY                 34 // U8     RGBs' values on the format R G B
#define ADD_REG_COLOR_ARRAY_BUS0            35 // U8     RGBs' values for the bus 0 on the format R G B
#define ADD_REG_COLOR_ARRAY_BUS1            36 // U8     RGBs' values for the bus 1 on the format R G B
#define ADD_REG_COLOR_OFF                   37 // U8     RGBs' values when the BUS is in off mode
#define ADD_REG_RESERVED1                   38 // U8     
#define ADD_REG_DI0_CONF                    39 // U8     Configuration of the digital input 0 (DI0)
#define ADD_REG_DO0_CONF                    40 // U8     Configuration of the digital output 0 (DO0)
#define ADD_REG_DO1_CONF                    41 // U8     Configuration of the digital output 1 (DO1)
#define ADD_REG_RESERVED2                   42 // U8     
#define ADD_REG_LATCH_NEXT_UPDATE           43 // U8     Any value above 0 will latch the next LED array update
#define ADD_REG_INPUTS_STATE                44 // U8     Read the correspondent input pin
#define ADD_REG_OUTPUTS_SET                 45 // U8     Set the correspondent output
#define ADD_REG_OUTPUTS_CLEAR               46 // U8     Clear the correspondent output
#define ADD_REG_OUTPUTS_TOGGLE              47 // U8     Toggle the correspondent output
#define ADD_REG_OUTPUTS_OUT                 48 // U8     Control the correspondent output
#define ADD_REG_PULSE_PERIOD                49 // U16    Period of pulses (ms)
#define ADD_REG_PULSE_COUNT                 50 // U8     Number of pulses to be performed -- write different than 0 to start
#define ADD_REG_EVNT_ENABLE                 51 // U8     Enable the Events

/************************************************************************/
/* PWM Generator registers' memory limits                               */
/*                                                                      */
/* DON'T change the APP_REGS_ADD_MIN value !!!                          */
/* DON'T change these names !!!                                         */
/************************************************************************/
/* Memory limits */
#define APP_REGS_ADD_MIN                    0x20
#define APP_REGS_ADD_MAX                    0x33
#define APP_NBYTES_OF_REG_BANK              404

/************************************************************************/
/* Registers' bits                                                      */
/************************************************************************/
#define B_RGB_ON                           (1<<0)       // RGB to ON
#define B_RGB_OFF                          (1<<1)       // RGB to OFF
#define B_DEMO_MODE_ON                     (1<<2)       // Start demonstration mode
#define B_DEMO_MODE_OFF                    (1<<3)       // Stop demonstration mode
#define MSK_DI0_SEL                        (3<<0)       // 
#define GM_DI0_SYNC                        (0<<0)       // Use as a pure digital input
#define GM_DI0_RISE_UPDATE_RGBS            (1<<0)       // Update RGBs with a rising edge
#define GM_DI0_HIGH_RGBS_ON                (2<<0)       // Able to update RGBs when the pin is HIGH. Turn LEDs off when rising edge is detected.
#define MSK_DO_SEL                         (7<<0)       // 
#define GM_DO_DIG                          (0<<0)       // Use as a pure digital output
#define GM_DO_PULSE_WHEN_UPDATED           (1<<0)       // Pulse 1 ms when the RGBs are updated
#define GM_DO_PULSE_WHEN_ARRAY_LOADED      (2<<0)       // Pulse 1 ms when a new color array is loaded
#define GM_DO_TOGGLE_WHEN_UPDATED          (3<<0)       // Toggles when the RGBs are updated
#define GM_DO_TOGGLE_WHEN_ARRAY_LOADED     (4<<0)       // Toggles when a new color array is loaded
#define B_DI0                              (1<<0)       // 
#define B_DO0                              (1<<0)       // 
#define B_DO1                              (1<<1)       // 
#define B_DO2                              (1<<2)       // 
#define B_DO3                              (1<<3)       // 
#define B_DO4                              (1<<4)       // 
#define B_EVT_LED_STATUS                   (1<<0)       // Event of register EVT_LED_STATUS
#define B_EVT_INPUTS_STATE                 (1<<1)       // Event of register EVT_INPUTS_STATE

#endif /* _APP_REGS_H_ */

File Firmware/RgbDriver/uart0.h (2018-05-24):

#ifndef _UART0_H_
#define _UART0_H_

#include "cpu.h"


/************************************************************************/
/* UART definitions                                                     */
/************************************************************************/
#define UART0_RX_INT_LEVEL		INT_LEVEL_LOW
#define UART0_TX_INT_LEVEL		INT_LEVEL_LOW
#define UART0_CTS_INT_LEVEL	    INT_LEVEL_LOW

#define UART0_RXBUFSIZ			1024
#define UART0_TXBUFSIZ			32

#define UART0_UART				USARTD0
#define UART0_PORT				PORTD
#define UART0_DATA				USARTD0_DATA
#define UART0_RX_pin			2
#define UART0_TX_pin			3

#define UART0_RX_ROUTINE_		ISR(USARTD0_RXC_vect, ISR_NAKED)
#define UART0_TX_ROUTINE_		ISR(USARTD0_DRE_vect, ISR_NAKED)


#define UART0_USE_FLOW_CONTROL	// comment this line if don't use
#define UART0_RTS_PORT			PORTD
#define UART0_RTS_pin			1
#define UART0_CTS_PORT			PORTD
#define UART0_CTS_pin			0

#define UART0_CTS_ROUTINE_		ISR(PORTD_INT0_vect, ISR_NAKED)
#define UART0_CTS_INT_N			0

#define uart0_leave_interrupt /*return*/reti()

/************************************************************************/
/* Prototypes                                                           */
/************************************************************************/
#define disable_uart0_rx set_io(UART0_RTS_PORT, UART0_RTS_pin);
#define enable_uart0_rx	 clear_io(UART0_RTS_PORT, UART0_RTS_pin);

void uart0_init(uint16_t BSEL, int8_t BSCALE, bool use_clk2x);
void uart0_enable(void);
void uart0_disable();
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

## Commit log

2018-05-24 Added the first files of the master microcontroller.
    [registers.xls]
2018-05-24 Increased reliability on the LEDS_READY interrupts.
2018-05-24 Change status events to UART instead of digital pins. Renamed pins to DUMMY. Renamed register bits. Added the rest of the functionalities (except the digital outputs handling).
    [registers.xls]
2018-05-24 Changed register LEDS_ON_BUS definition: it contains the number of LEDs on each bus.
    [registers.xls]
2018-06-03 Renamed firmware folder Rgb to RgbArray.
    [registers.xls]
2018-06-27 Replaced reserved register with registers for the pulse feature.
    [registers.xls]
2018-06-27 Added register for the new functionality: latch array without update the RGB array.
    [registers.xls]
2019-01-25 Added new register COLOR_OFF and the hability to configure the values when in standaby state.
    [registers.xls]
2022-12-17 Add PCB and BOM files
    [harp RBG array v1.0.brd, harp RBG array v1.0.sch, harp RBG array v1.0_BOM.xlsx]
2022-12-23 refactor repository structure
    [harp RBG array v1.0.brd, harp RBG array v1.0.sch, harp RBG array v1.0_BOM.xlsx]
2023-08-23 Update PCB asset image
2024-11-10 Update device schema source
